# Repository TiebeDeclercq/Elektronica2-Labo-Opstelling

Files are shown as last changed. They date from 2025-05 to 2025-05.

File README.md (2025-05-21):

# Elektronica2-Labo-Opstelling

Complete printplaat met alle schakelingen van zowel gelijkrichting als opamps @Vives kortrijk
Met een printbare voet voor betere stabiliteit en geen kortsluiting te krijgen.
Op deze voet wordt er gewerkt met heated inserts (M3) voor het monteren van de print.

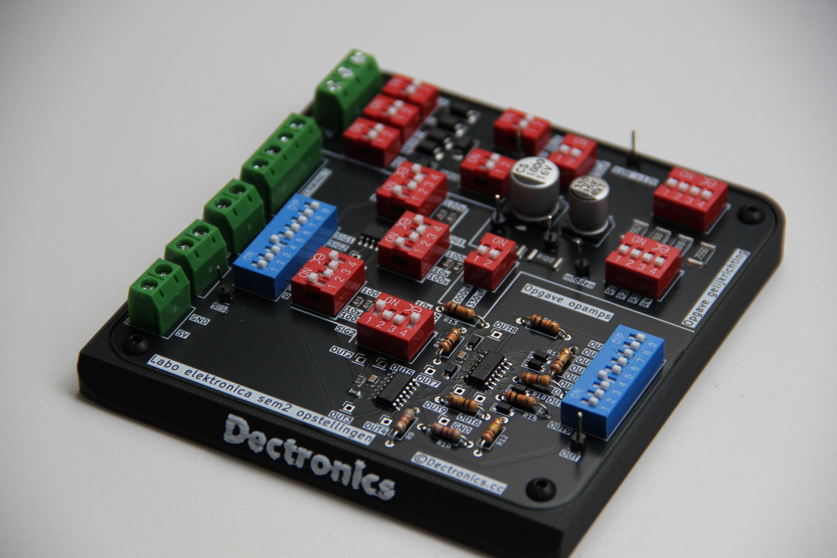
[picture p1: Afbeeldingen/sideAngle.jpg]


Het schema is als volgt:



Voor het solderen kan je gebruikmaken van de meegeleverde BOM file, alle componenten zijn 0805 buiten sommige TH componenten (omdat deze eigen keuze zijn en makkelijk te verangen moeten zijn)

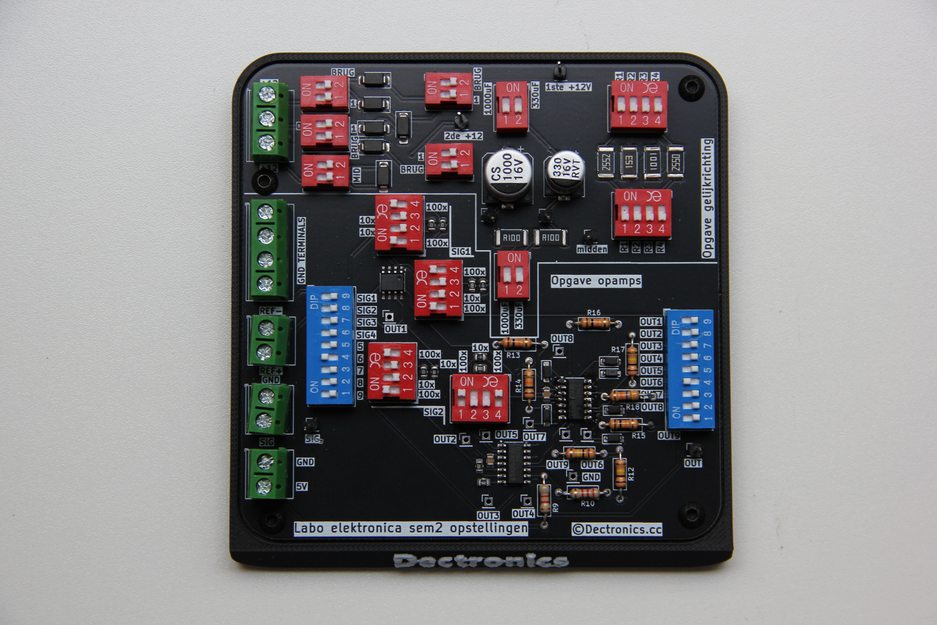
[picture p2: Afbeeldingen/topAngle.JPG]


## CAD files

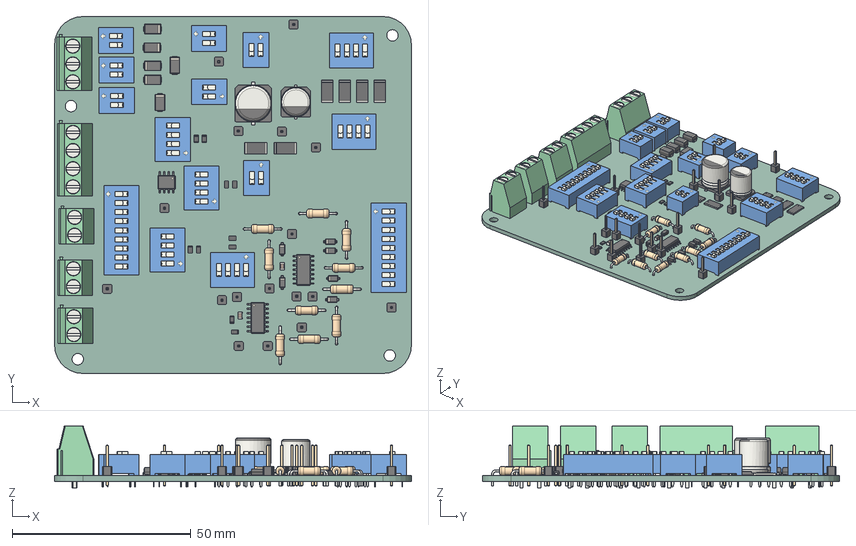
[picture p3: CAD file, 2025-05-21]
Elektronica 2 opstellingen/Elektronica 2 opstellingen.step
100.0 x 100.0 x 17.3 mm
R_0805_2012Metric x 10
R_2512_6332Metric x 6
R_Axial_DIN0207_L63mm_D25mm_P1016mm_Horizontal x 10
SW_DIP_SPSTx04_Slide_978x1234mm_W762mm_P254mm x 6
PinHeader_1x01_P254mm_Vertical x 17
D_SOD_123 x 6
SW_DIP_SPSTx02_Slide_978x726mm_W762mm_P254mm x 7
C_0805_2012Metric x 2
TerminalBlock_Phoenix_MKDS_15_2_1x02_P500mm_Horizontal x 3
D_SMA x 6
CP_Elec_10x105
TerminalBlock_Phoenix_MKDS_15_3_1x03_P500mm_Horizontal
SOIC_14_39x87mm_P127mm x 2
SW_DIP_SPSTx09_Slide_978x2504mm_W762mm_P254mm x 2
CP_Elec_8x10
TerminalBlock_Phoenix_MKDS_15_4_508_1x04_P508mm_Horizontal
SOIC_8_39x49mm_P127mm
Patje zuig men kloten_PCB

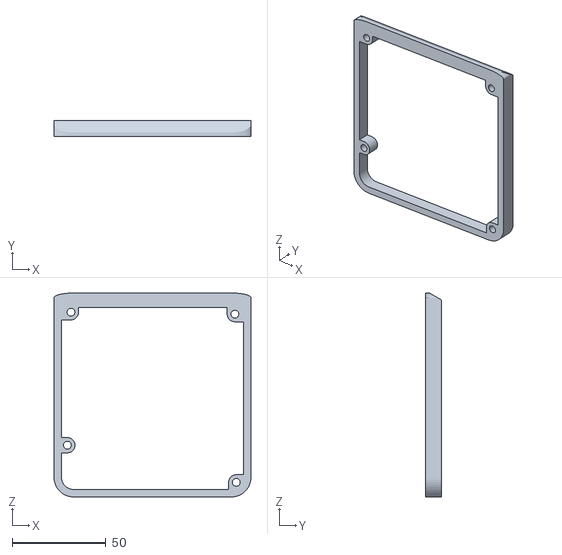
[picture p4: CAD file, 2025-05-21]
Printfiles/HouderPrintplaatElektronicaOpstellingen.stl
105.0 x 8.60 x 108.7

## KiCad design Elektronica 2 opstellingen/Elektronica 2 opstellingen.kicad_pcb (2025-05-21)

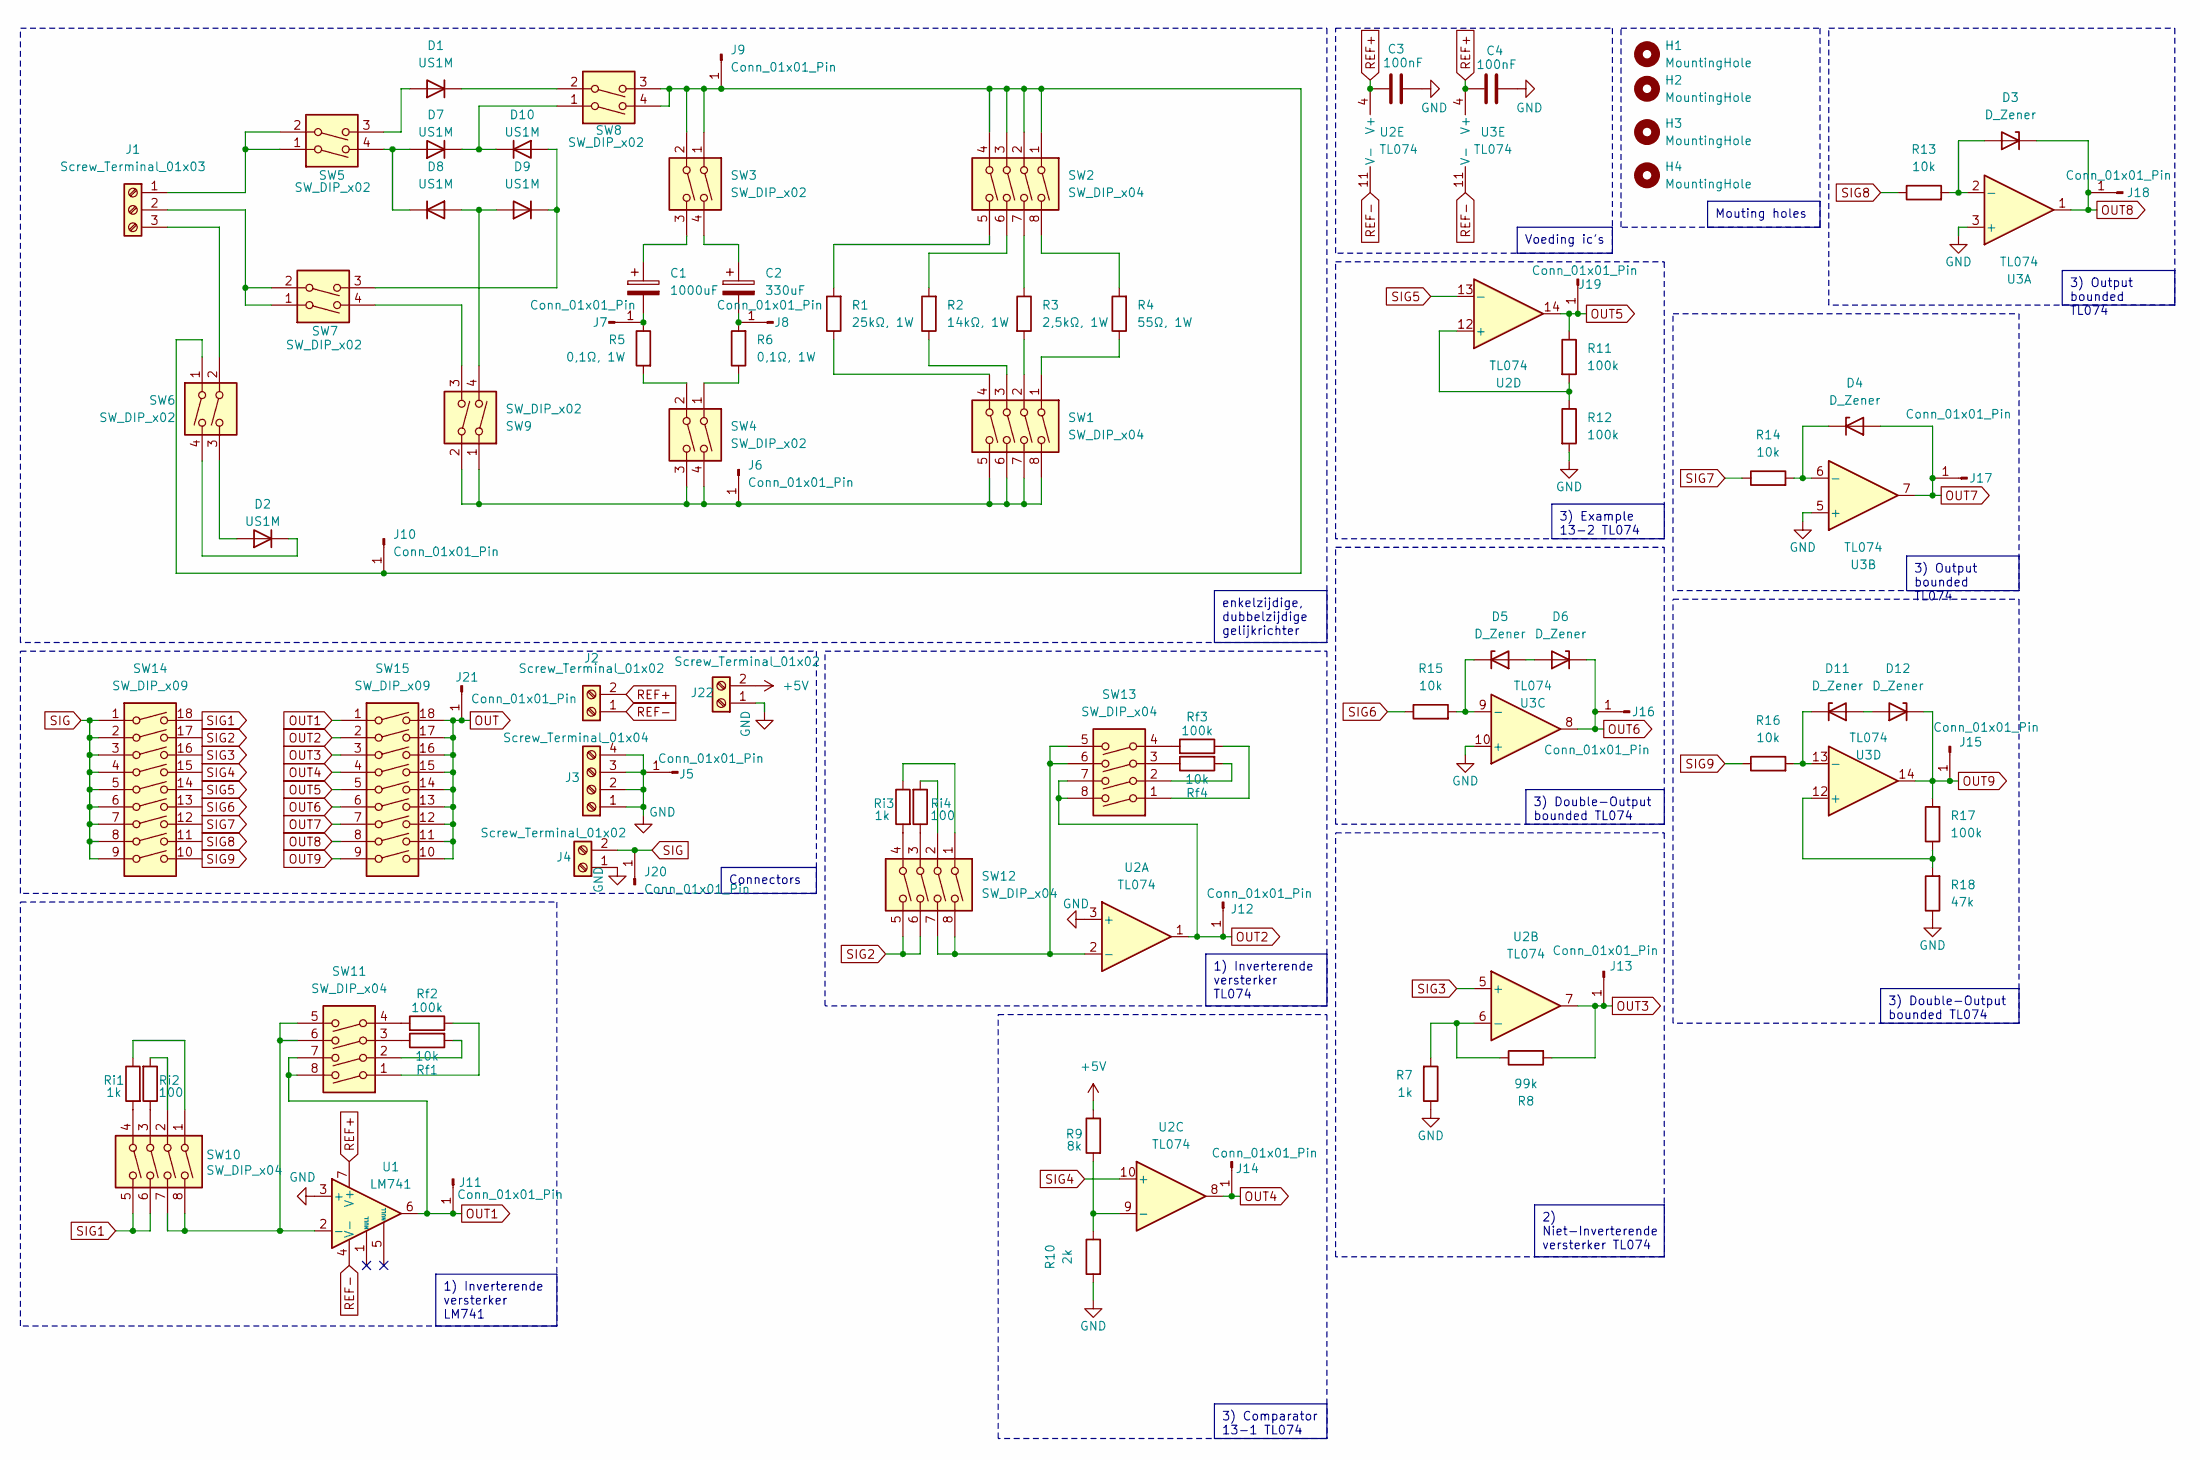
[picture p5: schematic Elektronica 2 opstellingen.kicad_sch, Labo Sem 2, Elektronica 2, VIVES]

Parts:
C1: 1000uF; CP_Elec_10x10.5
C2: 330uF; CP_Elec_8x10
C3, C4: 100nF; C_0805_2012Metric
D1, D2, D7, D8, D9, D10: US1M; D_SMA
D3, D4, D5, D6, D11, D12: D_Zener; D_SOD-123
H1, H2, H3, H4: MountingHole; MountingHole_3.2mm_M3
J1: Screw_Terminal_01x03; TerminalBlock_Phoenix_MKDS-1,5-3_1x03_P5.00mm_Horizontal
J2, J4, J22: Screw_Terminal_01x02; TerminalBlock_Phoenix_MKDS-1,5-2_1x02_P5.00mm_Horizontal
J3: Screw_Terminal_01x04; TerminalBlock_Phoenix_MKDS-1,5-4-5.08_1x04_P5.08mm_Horizont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
J5, J6, J7, J8, J9, J10, J11, J12, J13, J14, J15, J16, J17, J18, J19, J20, J21: Conn_01x01_Pin; PinHeader_1x01_P2.54mm_Vertical
R1: 25kΩ, 1W; R_2512_6332Metric
R2: 14kΩ, 1W; R_2512_6332Metric
R3: 2,5kΩ, 1W; R_2512_6332Metric
R4: 55Ω, 1W; R_2512_6332Metric
R5, R6: 0,1Ω, 1W; R_2512_6332Metric
R7: 1k; R_0805_2012Metric
R8: 99k; R_0805_2012Metric
R9: 8k; R_Axial_DIN0207_L6.3mm_D2.5mm_P10.16mm_Horizontal
R10: 2k; R_Axial_DIN0207_L6.3mm_D2.5mm_P10.16mm_Horizontal
R11, R12, R17: 100k; R_Axial_DIN0207_L6.3mm_D2.5mm_P10.16mm_Horizontal
R13, R14, R15, R16: 10k; R_Axial_DIN0207_L6.3mm_D2.5mm_P10.16mm_Horizontal
R18: 47k; R_Axial_DIN0207_L6.3mm_D2.5mm_P10.16mm_Horizontal
Rf1, Rf4: 10k; R_0805_2012Metric
Rf2, Rf3: 100k; R_0805_2012Metric
Ri1, Ri3: 1k; R_0805_2012Metric
Ri2, Ri4: 100; R_0805_2012Metric
SW1, SW2, SW10, SW11, SW12, SW13: SW_DIP_x04; SW_DIP_SPSTx04_Slide_9.78x12.34mm_W7.62mm_P2.54mm
SW3, SW4, SW5, SW6, SW7, SW8, SW9: SW_DIP_x02; SW_DIP_SPSTx02_Slide_9.78x7.26mm_W7.62mm_P2.54mm
SW14, SW15: SW_DIP_x09; SW_DIP_SPSTx09_Slide_9.78x25.04mm_W7.62mm_P2.54mm
U1: LM741; SOIC-8_3.9x4.9mm_P1.27mm
U2, U3: TL074; SOIC-14_3.9x8.7mm_P1.27mm

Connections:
+5V: J22.2, R9.1
GND: C3.2, C4.2, J3.1, J3.2, J3.3, J3.4, J4.1, J5.1, J22.1, R7.1, R10.2, R12.2, R18.1, U1.3 (+), U2.3 (+), U3.3 (+), U3.5 (+), U3.10 (+)
unnamed: C1.1, SW3.3
unnamed: C2.1, SW3.4
unnamed: D1.2 (A), SW5.3
unnamed: D1.1 (K), SW8.2
unnamed: D2.2 (A), SW6.3
unnamed: D2.1 (K), SW6.4
unnamed: D3.2 (A), R13.2, U3.2 (-)
unnamed: D4.1 (K), R14.2, U3.6 (-)
unnamed: D5.2 (A), D6.2 (A)
unnamed: D5.1 (K), R15.2, U3.9 (-)
unnamed: D7.2 (A), D8.1 (K), SW5.4
unnamed: D8.2 (A), D9.2 (A), SW9.4
unnamed: D9.1 (K), D10.2 (A), SW7.3
unnamed: D7.1 (K), D10.1 (K), SW8.1
unnamed: D11.2 (A), D12.2 (A)
unnamed: D11.1 (K), R16.2, U3.13 (-)
unnamed: J1.1, SW5.1, SW5.2
unnamed: J1.2, SW7.1, SW7.2
unnamed: J1.3, SW6.2
unnamed: J6.1, SW1.5, SW1.6, SW1.7, SW1.8, SW4.3, SW4.4, SW9.1, SW9.2
unnamed: C1.2, J7.1, R5.1
unnamed: C2.2, J8.1, R6.2
unnamed: J9.1, J10.1, SW2.1, SW2.2, SW2.3, SW2.4, SW3.1, SW3.2, SW6.1, SW8.3, SW8.4
unnamed: R1.1, SW1.4
unnamed: R1.2, SW2.5
unnamed: R2.1, SW1.3
unnamed: R2.2, SW2.6
unnamed: R3.1, SW2.7
unnamed: R3.2, SW1.2
unnamed: R4.1, SW1.1
unnamed: R4.2, SW2.8
unnamed: R5.2, SW4.2
unnamed: R6.1, SW4.1
unnamed: Rf1.1, SW11.3
unnamed: Rf1.2, SW11.2
unnamed: Rf2.1, SW11.1
unnamed: Rf2.2, SW11.4
unnamed: Rf3.1, SW13.1
unnamed: Rf3.2, SW13.4
unnamed: Rf4.1, SW13.3
unnamed: Rf4.2, SW13.2
unnamed: Ri1.1, SW10.1
unnamed: Ri1.2, SW10.4
unnamed: Ri2.1, SW10.3
unnamed: Ri2.2, SW10.2
unnamed: Ri3.1, SW12.1
unnamed: Ri3.2, SW12.4
unnamed: Ri4.1, SW12.3
unnamed: Ri4.2, SW12.2
unnamed: SW7.4, SW9.3
unnamed: SW10.7, SW10.8, SW11.5, SW11.6, U1.2 (-)
unnamed: SW12.7, SW12.8, SW13.5, SW13.6, U2.2 (-)
unnamed: R7.2, R8.1, U2.6 (-)
unnamed: R9.2, R10.1, U2.9 (-)
unnamed: R11.2, R12.1, U2.12 (+)
unnamed: R17.1, R18.2, U3.12 (+)
OUT: J21.1, SW15.10, SW15.11, SW15.12, SW15.13, SW15.14, SW15.15, SW15.16, SW15.17, SW15.18
OUT1: J11.1, SW11.7, SW11.8, SW15.1, U1.6
OUT2: J12.1, SW13.7, SW13.8, SW15.2, U2.1
OUT3: J13.1, R8.2, SW15.3, U2.7
OUT4: J14.1, SW15.4, U2.8
OUT5: J19.1, R11.1, SW15.5, U2.14
OUT6: D6.1 (K), J16.1, SW15.6, U3.8
OUT7: D4.2 (A), J17.1, SW15.7, U3.7
OUT8: D3.1 (K), J18.1, SW15.8, U3.1
OUT9: D12.1 (K), J15.1, R17.2, SW15.9, U3.14
REF+: C3.1, C4.1, J2.2, U1.7 (V+), U2.4 (V+), U3.4 (V+)
REF-: J2.1, U1.4 (V-), U2.11 (V-), U3.11 (V-)
SIG: J4.2, J20.1, SW14.1, SW14.2, SW14.3, SW14.4, SW14.5, SW14.6, SW14.7, SW14.8, SW14.9
SIG1: SW10.5, SW10.6, SW14.18
SIG2: SW12.5, SW12.6, SW14.17
SIG3: SW14.16, U2.5 (+)
SIG4: SW14.15, U2.10 (+)
SIG5: SW14.14, U2.13 (-)
SIG6: R15.1, SW14.13
SIG7: R14.1, SW14.12
SIG8: R13.1, SW14.11
SIG9: R16.1, SW14.10

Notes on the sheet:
3) Output bounded TL074
3) Comparator 13-1 TL074
3) Double-Output bounded TL074
Voeding ic's
Connectors
Mouting holes
1) Inverterende versterker LM741
enkelzijdige, dubbelzijdige gelijkrichter
3) Example 13-2 TL074
2) Niet-Inverterende versterker TL074
1) Inverterende versterker TL074

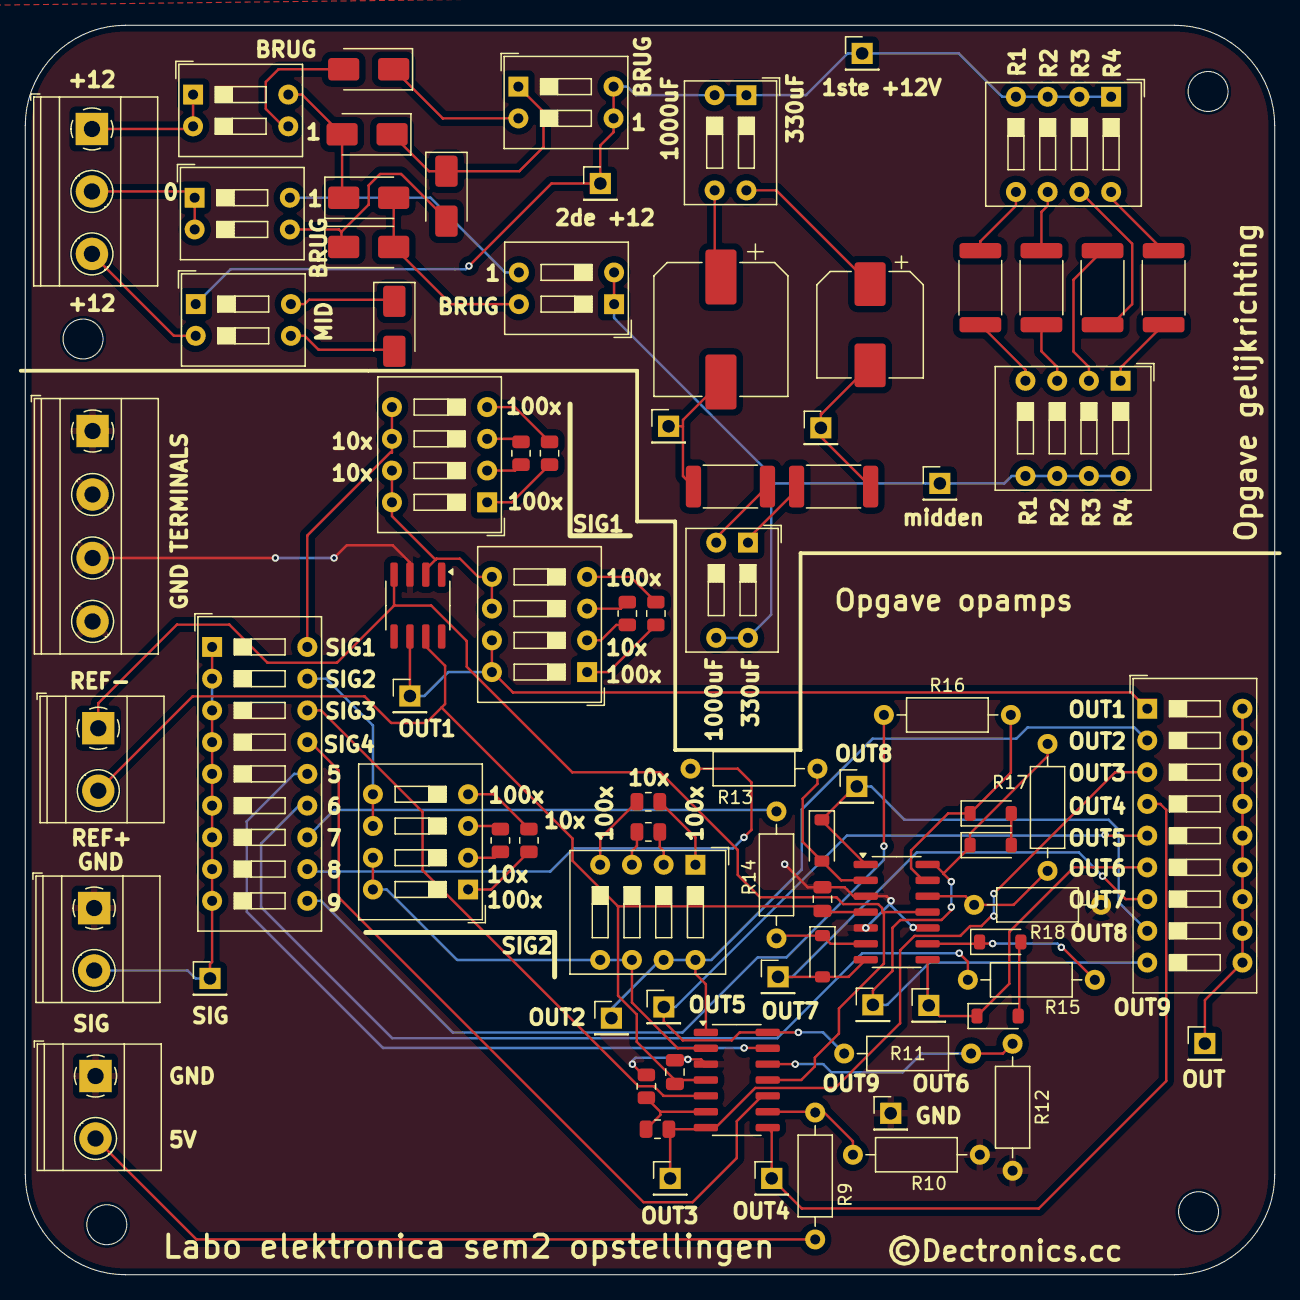
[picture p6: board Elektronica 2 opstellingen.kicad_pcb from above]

Board: 2 copper layers, 100.0 x 100.0 mm, 86 parts (0 on the bottom side), 80 nets.

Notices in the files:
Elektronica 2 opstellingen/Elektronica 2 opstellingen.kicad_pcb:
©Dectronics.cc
